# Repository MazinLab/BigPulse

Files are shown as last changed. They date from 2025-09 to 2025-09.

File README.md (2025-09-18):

# BigPulse
A high power avalanche mode laser driver

For fully isolated use, cut the jumper on the bottom, do not populate the boost converter and supply 200V and 12V to each side seperately

For use without ground isolation do not populate anything on the bottom other than the sense resistors and supply 12V through the barrel jack

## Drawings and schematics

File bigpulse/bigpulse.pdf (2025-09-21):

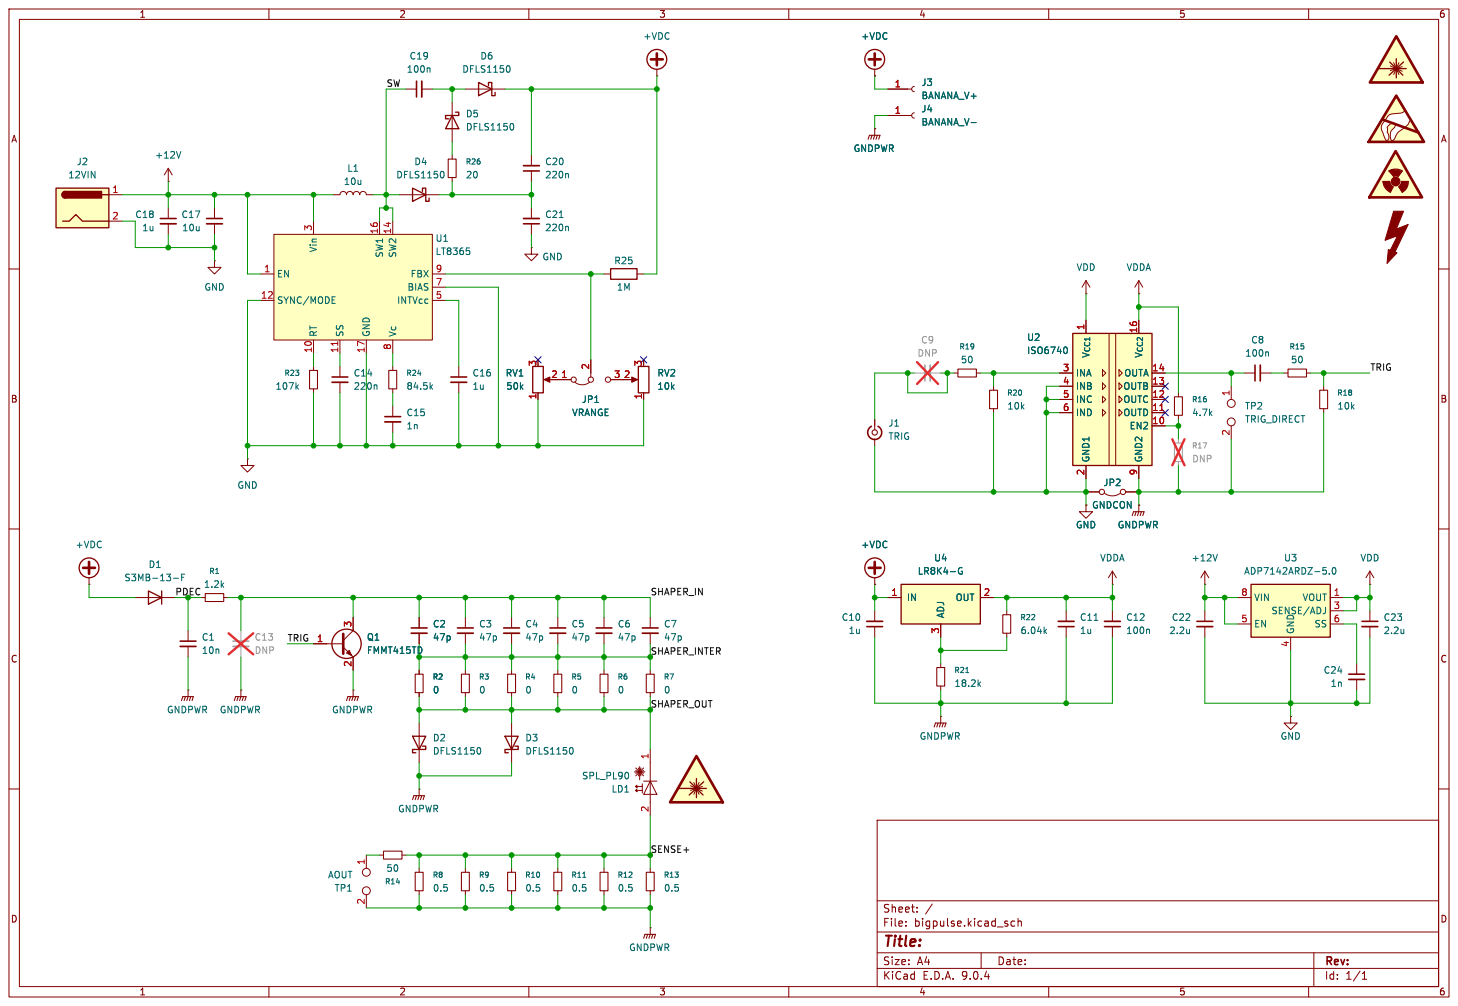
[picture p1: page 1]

3 RT 10 SS 11 GND 17 SW1 16 SW2 14 Vc 8 FBX 9 BIAS 7

9 OUTA 14 OUTB 13 OUTC 12 OUTD 11 EN2 10 U2
ISO6740

9 OUTA 14 OUTB 13 OUTC 12 OUTD 11 EN2 10

4 VOUT 1 SENSE/ADJ 3 SS 6 U3 ADP7142ARDZ-5.0 VDD

Id: 1/1 Title: File: bigpulse.kicad_sch Sheet: /

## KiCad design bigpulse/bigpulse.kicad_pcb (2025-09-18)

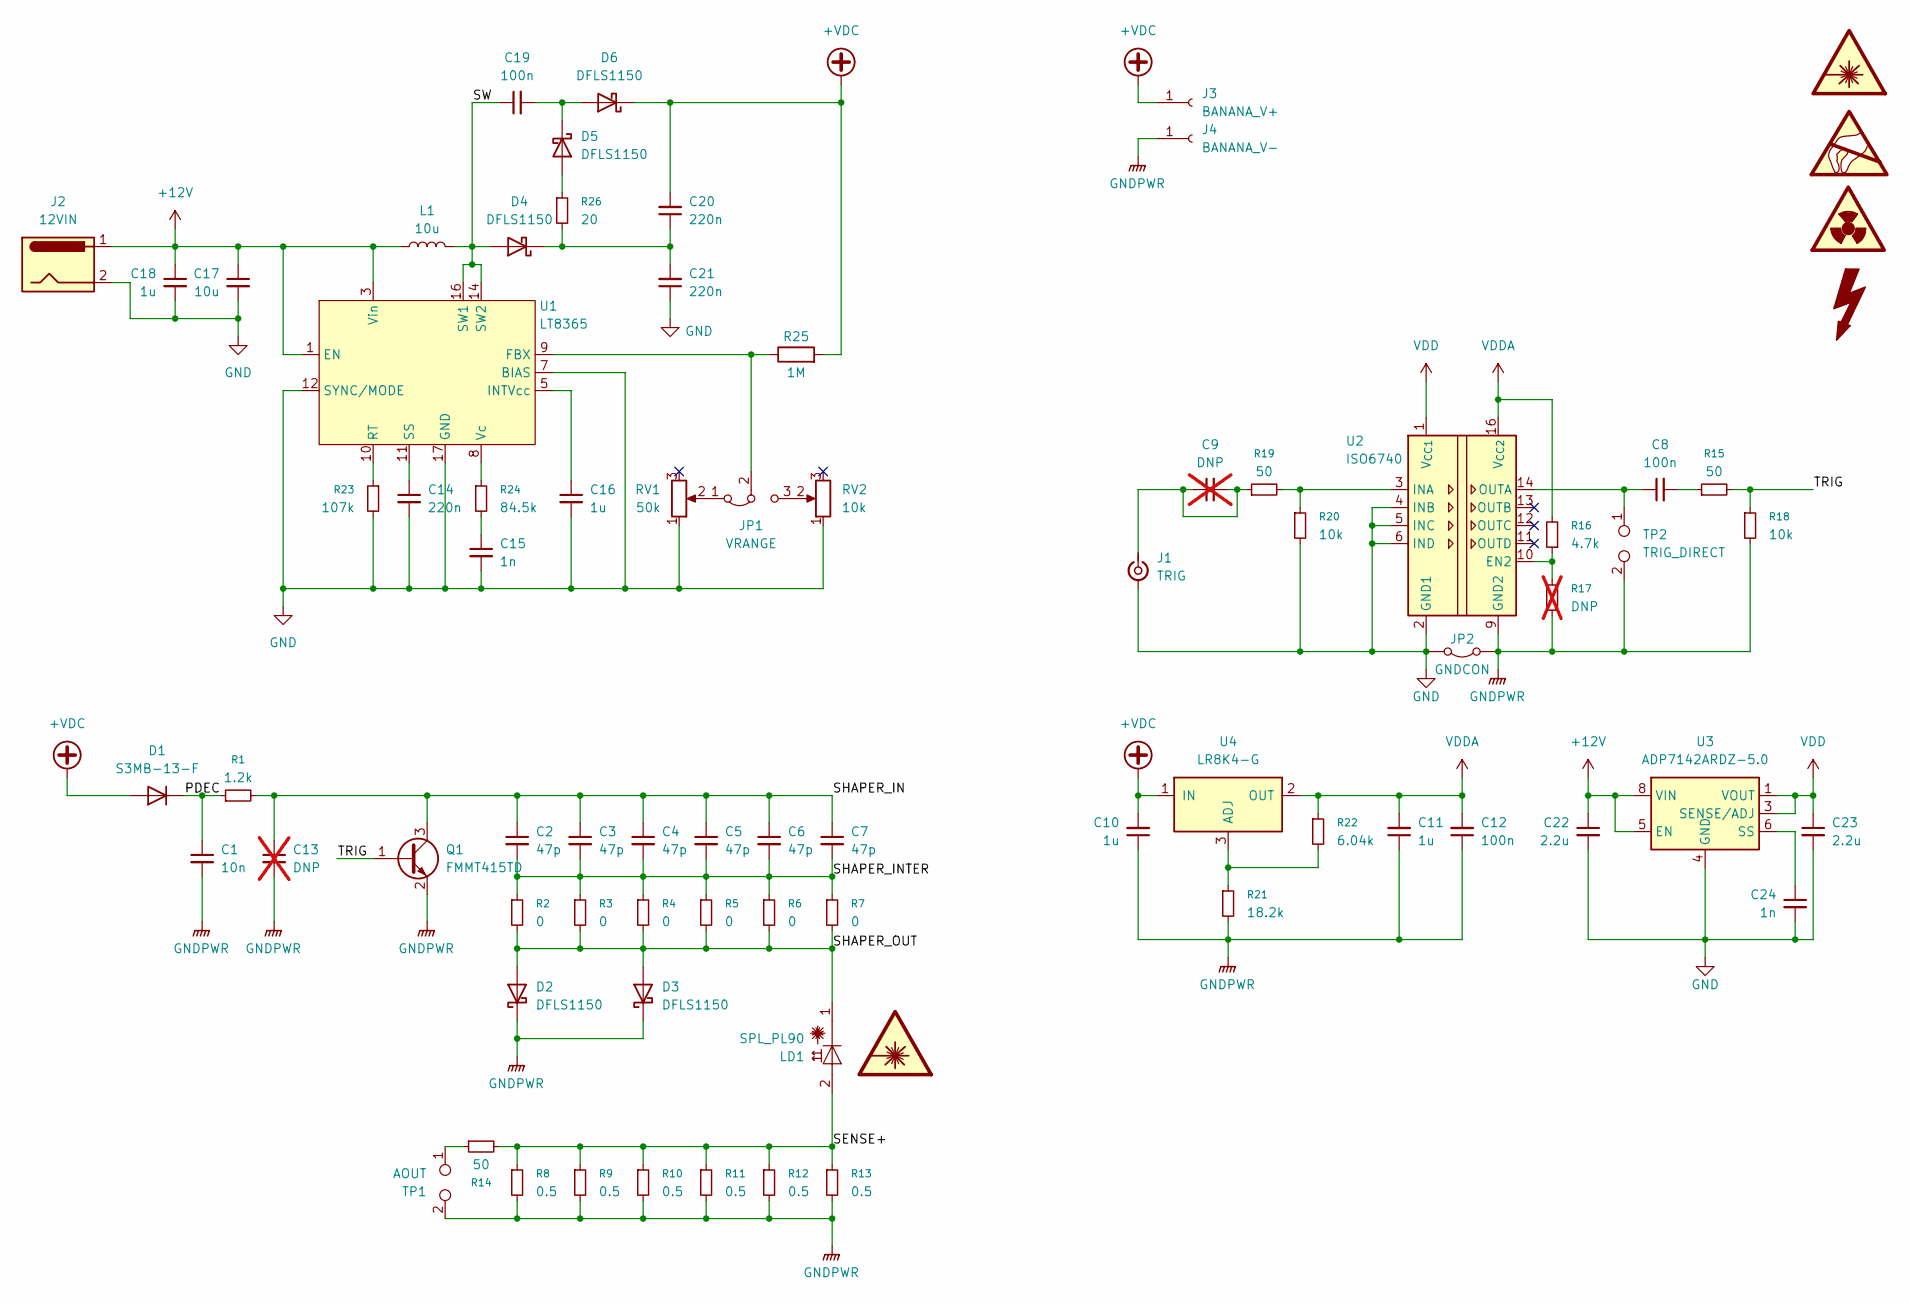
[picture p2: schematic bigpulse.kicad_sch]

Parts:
C1: 10n; C_1210_3225Metric; DIGIKEY_PN 709-VPDF102W103K1GV001ECT-ND
C2, C3, C4, C5, C6, C7: 47p; C_1210_3225Metric; DIGIKEY_PN 720-1040-1-ND
C8, C12, C19: 100n; C_1210_3225Metric; DIGIKEY_PN 445-2300-1-ND
C9: DNP; C_0603_1608Metric; not fitted
C10, C18: 1u; C_2220_5750Metric; DIGIKEY_PN 478-KGF55DR72J105KVCT-ND
C11, C16: 1u; C_0603_1608Metric; DIGIKEY_PN 1276-1946-1-ND
C13: DNP; C_1210_3225Metric; not fitted
C14: 220n; C_0603_1608Metric; DIGIKEY_PN 490-5402-1-ND
C15, C24: 1n; C_0603_1608Metric; DIGIKEY_PN 399-C0603C102K5RACTUCT-ND
C17: 10u; C_2220_5750Metric; DIGIKEY_PN 478-KGM55DR72A106MVCT-ND
C20, C21: 220n; C_2220_5750Metric; DIGIKEY_PN 490-3520-1-ND
C22, C23: 2.2u; C_0603_1608Metric; DIGIKEY_PN 490-GRM188Z71E225ME43DCT-ND
D1: S3MB-13-F; D_SMB; DIGIKEY_PN S3MB-FDICT-ND
D2, D3, D4, D5, D6: DFLS1150; D_PowerDI-123; DIGIKEY_PN DFLS1150Q-7DICT-ND
J1: TRIG; SMA_Amphenol_132134-10_Vertical; DIGIKEY_PN 132134-10
J2: 12VIN; BarrelJack_Wuerth_694106106102_2.0x5.5mm; DIGIKEY_PN 732-5929-1-ND
J3: BANANA_V+; MountingHole_3.7mm_Pad_Via; DIGIKEY_PN J10125-ND
J4: BANANA_V-; MountingHole_3.7mm_Pad_Via; DIGIKEY_PN J10126-ND
JP1: VRANGE; SolderJumper-3_P1.3mm_Bridged2Bar12_Pad1.0x1.5mm
JP2: GNDCON; SolderJumper-2_P1.3mm_Bridged_Pad1.0x1.5mm
L1: 10u; L_Wurth_WE-LQSH-4020; DIGIKEY_PN 732-3336-1-ND
LD1: SPL_PL90; LED_D5.0mm; DIGIKEY_PN 475-SPLPL90AT03-ND
Q1: FMMT415TD; SOT-23-3; DIGIKEY_PN FMMT415TDCT-ND
R1: 1.2k; R_1210_3225Metric; DIGIKEY_PN 2019-RK73B2ETTD122JCT-ND
R2, R3, R4, R5, R6, R7: 0; R_1210_3225Metric; DIGIKEY_PN RMCF1210ZT0R00CT-ND
R8, R9, R10, R11, R12, R13: 0.5; R_1210_3225Metric; DIGIKEY_PN 311-0.5NACT-ND
R14, R15, R19: 50; R_0603_1608Metric; DIGIKEY_PN 764-FC0603E50R0BTBST1CT-ND
R16: 4.7k; R_0603_1608Metric; DIGIKEY_PN 311-4.70KHRCT-ND
R17: DNP; R_0603_1608Metric; not fitted
R18, R20: 10k; R_0603_1608Metric; DIGIKEY_PN RMCF0603JT10K0CT-ND
R21: 18.2k; R_0603_1608Metric; DIGIKEY_PN RMCF0603FT18K2CT-ND
R22: 6.04k; R_0603_1608Metric; DIGIKEY_PN 2019-RK73H1JTTD6041FCT-ND
R23: 107k; R_0603_1608Metric; DIGIKEY_PN 311-107KHRCT-ND
R24: 84.5k; R_0603_1608Metric; DIGIKEY_PN 311-84.5KHRCT-ND
R25: 1M; R_0603_1608Metric; DIGIKEY_PN 2019-RN73H1JTTD1004B25CT-ND
R26: 20; R_0805_2012Metric; DIGIKEY_PN 738-RNCF0805DTE20R0CT-ND
RV1: 50k; Potentiometer_Bourns_3314S_Horizontal; DIGIKEY_PN 3314J-503ECT-ND
RV2: 10k; Potentiometer_Bourns_3314S_Horizontal; DIGIKEY_PN 3314J-103ECT-ND
TP1: AOUT; SMA_Amphenol_132134-10_Vertical; DIGIKEY_PN 132134-10
TP2: TRIG_DIRECT; SMA_Amphenol_132134-10_Vertical; DIGIKEY_PN 132134-10
U1: LT8365; Analog_MSOP-12-16-1EP_3x4.039mm_P0.5mm_EP1.651x2.845mm_Ther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; DIGIKEY_PN 505-LT8365EMSE#TRPBFCT-ND
U2: ISO6740; SOIC-16W_7.5x10.3mm_P1.27mm; DIGIKEY_PN 296-ISO6740QDWRQ1CT-ND
U3: ADP7142ARDZ-5.0; SOIC-8-1EP_3.9x4.9mm_P1.27mm_EP2.29x3mm; DIGIKEY_PN 505-ADP7142ARDZ-5.0-ND
U4: LR8K4-G; TO-252-2; DIGIKEY_PN LR8K4-GCT-ND

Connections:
+12V: C17.1, C18.1, C22.1, J2.1, L1.1, U1.1 (EN), U1.3 (Vin), U3.5 (EN), U3.7 (VIN), U3.8 (VIN)
+VDC: C10.2, C20.2, D1.2 (A), D6.1 (K), J3.1, R25.2, U4.1 (IN)
/PDEC: C1.1, D1.1 (K), R1.1
/SENSE+: LD1.2 (A), R8.1, R9.1, R10.1, R11.1, R12.1, R13.1, R14.2
/SHAPER_IN: C2.1, C3.1, C4.1, C5.1, C6.1, C7.1, C13.1, Q1.3 (C), R1.2
/SHAPER_INTER: C2.2, C3.2, C4.2, C5.2, C6.2, C7.2, R2.1, R3.1, R4.1, R5.1, R6.1, R7.1
/SHAPER_OUT: D2.2 (A), D3.2 (A), LD1.1 (C), R2.2, R3.2, R4.2, R5.2, R6.2, R7.2
/SW: C19.1, D4.2 (A), L1.2, U1.14 (SW2), U1.16 (SW1)
/TRIG: Q1.1 (B), R15.2, R18.1
GND: C14.2, C15.2, C16.2, C17.2, C18.2, C21.1, C22.2, C23.2, C24.2, J1.2 (Ext), J2.2, JP2.1 (A), R20.2, R23.2, RV1.1, RV2.1, U1.7 (BIAS), U1.12 (SYNC/MODE), U1.17 (GND), U2.2 (GND1), U2.4 (INB), U2.5 (INC), U2.6 (IND), U2.8 (GND1), U3.4 (GND), U3.9 (GND)
GNDPWR: C1.2, C10.1, C11.1, C12.1, C13.2, D2.1 (K), D3.1 (K), J4.1, JP2.2 (B), Q1.2 (E), R8.2, R9.2, R10.2, R11.2, R12.2, R13.2, R17.1, R18.2, R21.2, TP1.2, TP2.2, U2.9 (GND2), U2.15 (GND2)
unnamed: C8.2, R15.1
unnamed: C15.1, R24.2
unnamed: C20.1, C21.2, D4.1 (K), R26.2
unnamed: D5.2 (A), R26.1
unnamed: C19.2, D5.1 (K), D6.2 (A)
unnamed: C9.1, C9.2, J1.1 (In), R19.1
unnamed: JP1.1 (A), RV1.2
unnamed: JP1.3 (B), RV2.2
unnamed: JP1.2 (C), R25.1, U1.9 (FBX)
unnamed: R14.1, TP1.1
unnamed: C16.1, U1.5 (INTVcc)
unnamed: R23.1, U1.10 (RT)
unnamed: C14.1, U1.11 (SS)
unnamed: R24.1, U1.8 (Vc)
unnamed: R16.1, R17.2, U2.10 (EN2)
unnamed: R19.2, R20.1, U2.3 (INA)
unnamed: C8.1, TP2.1, U2.14 (OUTA)
unnamed: C24.1, U3.6 (SS)
unnamed: R21.1, R22.2, U4.3 (ADJ)
VDD: C23.1, U2.1 (V_{CC1}), U3.1 (VOUT), U3.2 (VOUT), U3.3 (SENSE/ADJ)
VDDA: C11.2, C12.2, R16.2, R22.1, U2.16 (V_{CC2}), U4.2 (OUT)

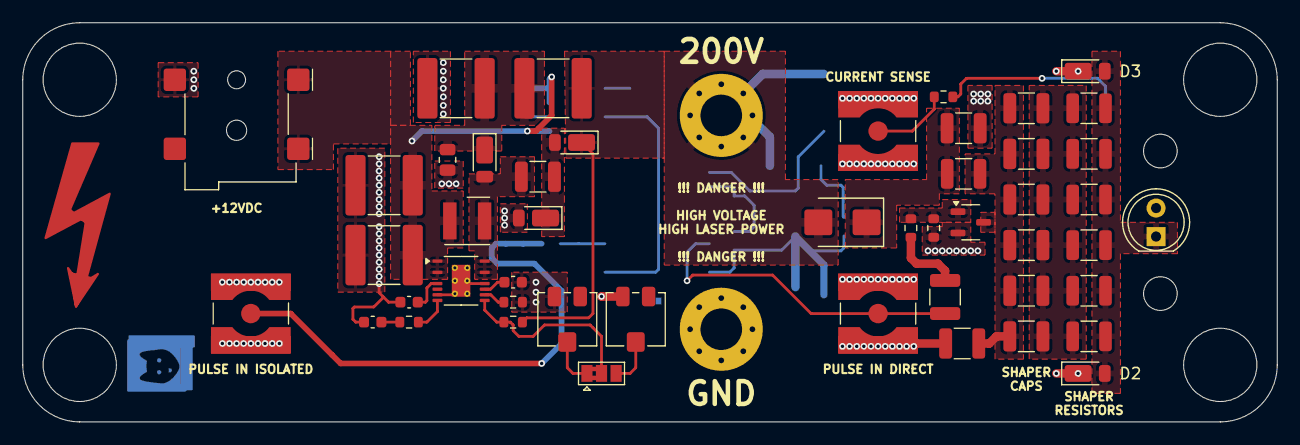
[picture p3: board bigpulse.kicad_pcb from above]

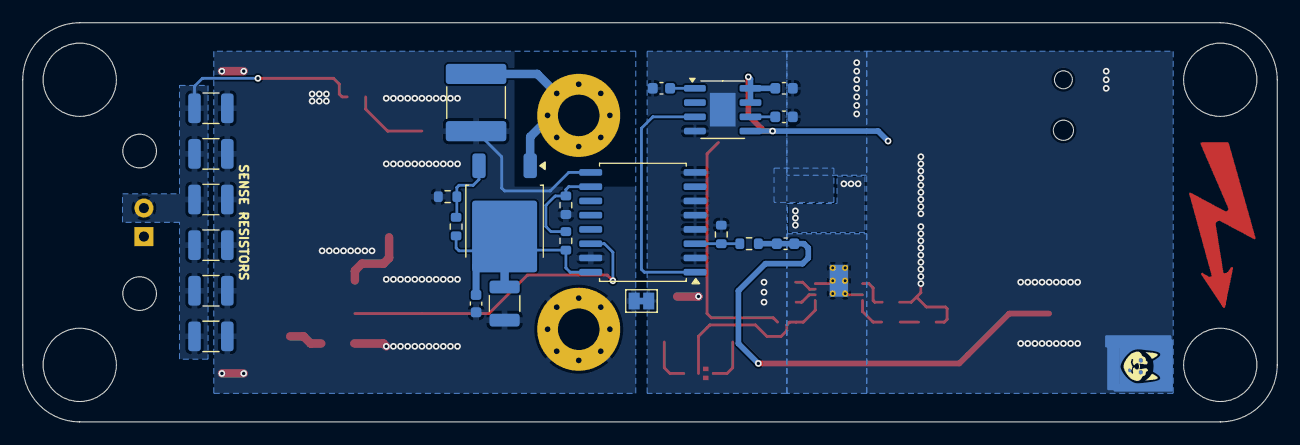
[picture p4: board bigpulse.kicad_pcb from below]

Board: 2 copper layers, 111.8 x 35.6 mm, 80 parts (24 on the bottom side), 32 nets.

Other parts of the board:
H**: 1/4 20; quarter-twenty
H**#2, H**#3, H**#4: 1/4 20; quarter-twenty
MH1, MH4: 4-40a; MountingHole_3mm
svg2mod: G***; milo
